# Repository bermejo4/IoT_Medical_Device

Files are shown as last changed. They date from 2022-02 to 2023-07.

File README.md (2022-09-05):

# IoT Medical Device Development:

## Objectives:
- Electronic wireless system to collect physiological data from a patient and deliver it to a server.
- Wireless. (without data cable or power cable)
- Low Cost.
- Small dimensions. 
- Show the information collected on the server.

## Steps: 
[Steps.md](https://github.com/bermejo4/Proyectos2/blob/main/Documentation/Steps.md)

## Costs:
[Costs.md](https://github.com/bermejo4/Proyectos2/blob/main/Documentation/Costs.md)

## Comparision between Raspberry Pico and Arduino Nano:
[ComparationBetween_RaspPico_ArduNano.md](https://github.com/bermejo4/Proyectos2/blob/main/Documentation/ComparationBetween_RaspPico_ArduNano.md)

## Pins-modules diagram:

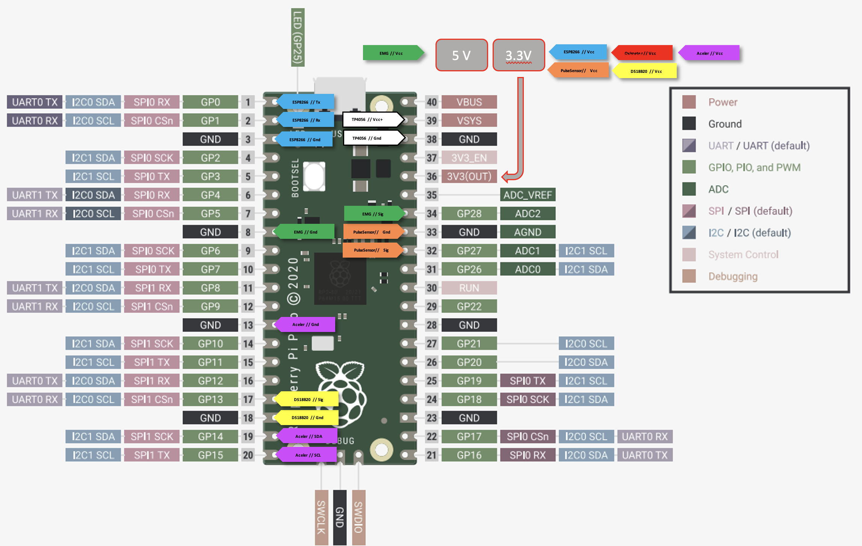
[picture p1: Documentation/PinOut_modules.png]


## Micropython code running on the Raspberry Pico:
[PicoClient/TCP_Send_info.py](https://github.com/bermejo4/Proyectos2/blob/main/PicoClient/TCP_Send_info.py)

## Server code:
[Server/tcp_graficador_pico.py ](https://github.com/bermejo4/Proyectos2/blob/main/Server/tcp_graficador_pico.py)

------
------
## Paper:

### Abstract
The aim of the present project is the development of a wireless, little size, low cost and scalable platform, based in IoT. It will be capable of measuring different physiological signals (temperature, pulse and movement) and internal device signals (temperature). Then, it will send them together in the same packet through Wi-Fi to a network, or the Internet, using the TCP/IP model to finally be received by a server and represented in a graphical format. The final use of it is to monitor patients in medical environments remotely by specialists.

### 1. Introduction
The Internet of Things (IoT) term refers to the collective network of connected devices and the technology that facilitates communication between devices and the cloud, as well as between the devices themselves [1]. In this context, Cisco states that IoT devices will account for 50
percent (14.7 billion) of all globally networked devices by 2023 [2].

There is no doubt that this technology is growing unstoppably and every day more companies and sectors incorporate it. One of the industries that will have to face this change will be the medical instrumentation industry to connect all its medical devices to the Internet, which, whatever their function, are ultimately intended to obtain very useful physiological data for later analysis and according to them an adequate decision making.

Nowadays, there is an abundance of proprietary IoT healthcare platforms, for example, Apple Watch Series 3 combined with “Health” App, or Samsung Galaxy Watch 4 and “Samsung Health” App, which can monitor the ECG, oximetry, steps or sleep. But these systems and devices are very expensive, with watches prices above 400$ and phones between 600$ and 1100$ (smartwatches can't work properly without a smartphone). In many cases, these products are not scalable or modifiable because don't provide open-source software or hardware, and technical documentation too. Also, they need to be connected through Bluetooth to the phone, so two connections (first Bluetooth, then Wi-Fi or 5G) must be established and the probabilities of failures increase. This architecture could be minimized by using only one connection to transfer data to the cloud.
Also, there are specialized healthcare monitoring IoT hardware platforms like Mysignals HW(Libelium). This device can collect a lot of physiological signals such as temperature, glucose in blood, electrocardiogram, electromyogram, etc. And all open source and scalable, due to it being based on Arduino. Another example of a multisensory hardware platform for measuring physiological signals is Bitalino, but it only works with Bluetooth and is too expensive, starting at 400$ the basic, being an educational platform. 
Nowadays, there is a tendency to create open-source IoT devices. The possible design of efficient medical IoT sensor nodes in terms of low-cost, low power consumption, and increased data accuracy based on open-source platforms are covered by Nikos Petrellis et al. [3]. Their solution is performed with an Arduino UNO attached to a Raspberry Pi, but the costs of these elements (together more than 60$ nowadays) are still high compared to this project objective. And Sugathan et al. [4] create a generic clothing technology to measure SPO2, electro dermal activity, and body temperature implemented with an Arduino Lily-pad, although they send data through serial communication and they don’t use a wireless model, indeed it's one of their future enhancements. 
From a broad point of view, the final destination of this project is the design and implementation of a platform based on IoT, improving the requirements followed by Nikos Petrellis, to monitor patients in a Hospital or old people's home in a non-intrusive way when it's not necessary.

### 2.	Technical Proposal
The main purpose is to develop a platform that reaches the following objectives:
- First, a wearable small size device with a wireless connection to transmit the data collected from its sensors, focusing on a TCP/IP model for that purpose.
- Second, a low cost system, using components easy to buy nowadays on the Internet and cheap compared with others actual similar models.
- Third, a concentrated multi-sensor device capable of measuring different physiological signals.
- Fourth, a scalable IoT project. Sensors could be replaced or added depending on pins available and the protocol connection used.
To fulfill these mentioned requirements, a system is designed based on the development of an IoT device to acquire physiological and internal device data by sensors; 
then the packeting (JSON) and transfer of them with a TCP/IP model and finally their reception in an extern server. 
The system process is as follows: 
1. Sensorization: This device works with 3 external sensors (temperature sensor, pulse sensor and accelerometer) and 1 internal sensor (MCU temperature).
The internal sensor helps to know how is the IoT device working and to control it. Knowing the temperature a problem with the device can be detected if the temperature grows extremely.
2. Data collection: sensors send  physical analog signal to the microcontroller which are sampled and quantified to transform them into manageable digital data. In some cases the signal is digitalized in an external module where the sensor is placed rather than in the microcontroller, in this case the microcontroller only has to collect the result following the communication protocol used by the module in question  (SPI, I2C, UART, or one of its own).
3. Formatting and Transfer: Once the microcontroller has the data, it must prepare them for shipment. It is important to detail a format for the shipment that is distinguishable later in the reception, clearly marking the distinction between data collected from different sensors. JSON, a text format for sending data, widely used, easy to handle both at source and destination, is used to send the data collected to the destination.
The data is packeting using TCP/IP headers and then sending to the network through Wi-Fi.
4. Reception: At the destination the data is unformat and stored differently depending on the sensor to which they belong. Subsequently, these data can be represented in many ways, using an array, a graph… In this case is represented using a real time graph.

### 3.	Architecture
The system architecture can be described from a topological network point of view, shown in Figure 1. 

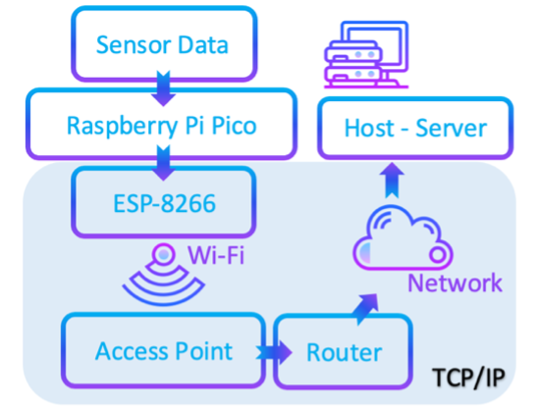
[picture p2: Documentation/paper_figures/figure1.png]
 

**Figure 1.** *Network topological architecture of the whole system.*

The device is set with an IP address and a port number. It transmits the information collected to an access point through Wi-Fi, and the access point sends the information to a router which decides where to send it. Once the information is sent through the Internet or a local network and then it arrives at the destination, a server.
This system uses TCP (Transmission Control Protocol) rather than UDP (User Datagram Protocol) to send the information to the remote host or server. The main differences between them are that TCP is a connection oriented and reliable protocol; and otherwise UDP is a connectionless and unreliable protocol. The data handled demands a reliable protocol because physiological data is dealt(it can be considered sensitive information). And an oriented connection protocol is needed because before to send the information the origin has to make sure that the destination is ready to receive it, although this kind of detail is less important than the reliable feature. Nevertheless, these TCP features pay its advantage in time, losing a little real time experience. It's true that UDP can be used implementing the TCP features in the application layer of TCP/IP model improving times, but also gaining more complexity, but this is out of the scope of this work.
An implementation detail to take account in the transfer step is the format of the information. All is encapsulated in a JSON format with the following shape:

```
{"Temp":"_","TempMcu":"_","PulseSig":"_","Acel_x":"_","Acel_y":"_","Acel_z":"_"}
```

Being the "_" the information of each field measured. Then, the destination knows this format and extract the information of each field to represent it properly.
When the information finally reaches the destination, it must be represented. For that purpose, a server code is written in Python that receive the data and represent it in a graphical format with the Matplotlib python library in real time. The server works with two threads, one has the task of receiving the data and save it, and the other thread represents the data in graphs, which are shown in the figure 2.

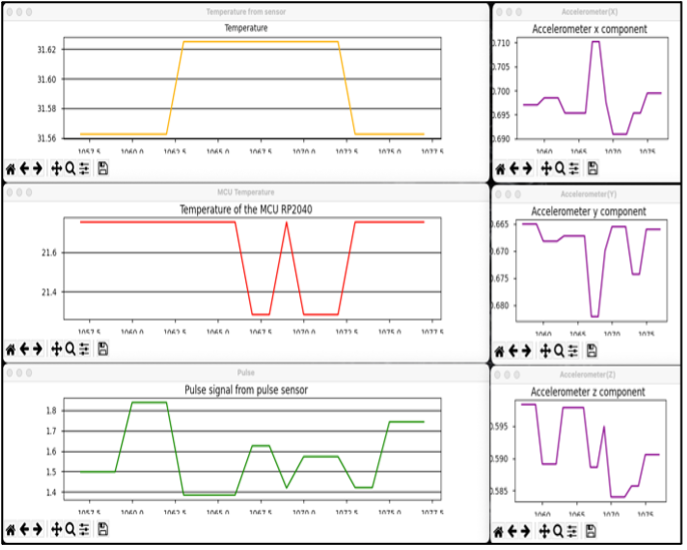
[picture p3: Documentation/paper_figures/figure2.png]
 

**Figure 2.** *Data representation with graphs.*

There are 6 graphs, one of the pulse sensor (green in Figure 2), another for the temperature (yellow in Figure 2), 3 for each of the axes of the accelerometer (purple in Figure 2) and other for the temperature of the mcu (red in the Figure 2). Each graph is represented in different windows, so the final user of the data can move and resize each graph depending on the screen size and which graph or graphs that are considered more important. Also, the Matplotlib frame representation gives some useful tools to manipulate the graphs. The server code is upload in [5].

### 4.	Implementation
The IoT device developed in this work uses:
**Temperature Sensor:** a sensor DS18B20 is used to measure the temperature which is connected to the Raspberry Pi Pico (GPIO 16) through a resistance of 4,7 kΩ (Figure 3 and Figure 6). It’s price is lower than 1$.

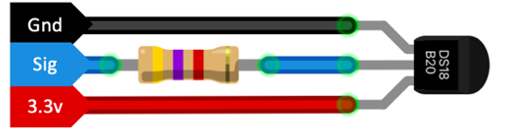
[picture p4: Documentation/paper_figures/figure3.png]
 

**Figure 3.** *DS18B20 connections with mcu.*

**Pulse Sensor:** to obtain the pulse a module called "Pulse Sensor for Arduino", built with an APDS-9008 photo sensor and MCP6001 Op-Amp, is connected directly to the pin 31 (ADC0) of the Raspberry Pi Pico. It sends an analogical signal to it, wire pink of the Figure 4. It’s price is around 1$ and 3$.

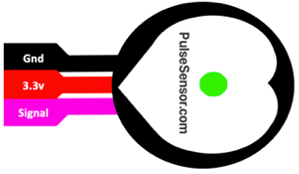
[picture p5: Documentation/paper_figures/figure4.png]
 

**Figure 4.** *Pulse Sensor connections with mcu.*

**Accelerometer:** To obtain the movements the MPU5060 board is used. It employs an I2C communication protocol, so it needs two I2C pins. The Slave Data Address pin (SDA) is connected to the pin SDA 19, and the Slave Clock pin (SCL) is connected to the pin SDA 20 (Figures 5 and 6). Its price is around 2$.

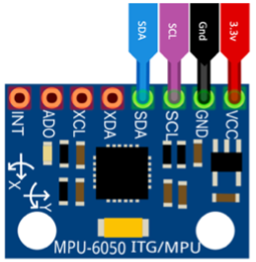
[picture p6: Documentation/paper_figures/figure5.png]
 

**Figure 5.**  *MPU5060 connections with mcu.*

**Microcontroller (mcu):** Raspberry Pi Pico has a dual core microcontroller chip (Rp2040) with a flexible clock of 133MHz, a SRAM of 264KB, 26 pins, 4 of it analog, two UART, two I2C and two SPI connections available. Also, there is a temperature sensor inside accessible with software to control mcu temperature. The price of this microcontroller is around 5$. All the connections are shown in the figure 6.
The Raspberry Pi Pico can be programmed with Micropython, C or C++. In this case the microcontroller has been programmed in Micropython, a lean and efficient implementation of the Python 3 programming language that includes a small subset of the Python standard library and is optimised to run on microcontrollers and in constrained environments.

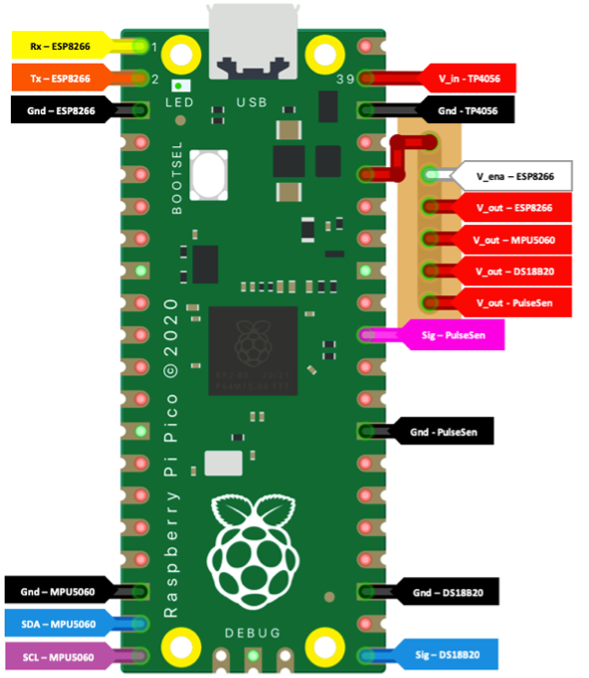
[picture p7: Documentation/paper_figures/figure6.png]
 

**Figure 6.** *Raspberry Pi Pico connections diagram.* 

**Wi-Fi Module:** The ESP8266 Module is used as a slave of the mcu through a UART connection. The connections of the wires must be done connecting Rx pin of the ESP8266 with the mcu Tx pin, and Tx of the ESP8266 with Rx mcu pin. Is necessary in some boards uses one pin of the ESP8266 fed with 3.3V to enable the UART mode (Figure 7). Its price is 1$.

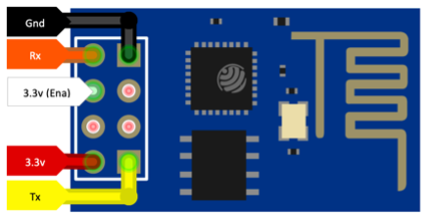
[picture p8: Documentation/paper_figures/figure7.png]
 

**Figure 7.** *ESP8266 connections with mcu, white wire enable UART mode.* 

The Wi-Fi module works with AT commands, which consists of a series of short text strings which can be combined to produce commands for operations such as dialing, hanging up, and changing the parameters of a connection; transmitted through the UART communication, so Micropython handles the commands in the form of strings to implement the corresponding communication protocol; some useful AT commands employed are: 
- AT: To test AT startup, also used to test the connection between the Raspberry Pi Pico and ESP8266.
- AT+CWJAP="Network_name","Password": To Search the Wi-Fi access point with the name "Network_name" and to connect to it with the password "Password".
- AT+CIPSTART="TCP","192.168.12.147",9999: To establish a TCP connection with a host or server with the IP address "192.168.12.147" and in the port "9999".
- AT+CIPSEND="Info_String": To send the information "Info_String" in the form of string through the connection established.

**Battery:** LiPo battery of 3.7 V, 1000 mAh, 10x20x50 mm size and its prize is around 5$. These features are very relevant, 3.7 V is the voltage that the microcontroller needs, dimensions match with its dimensions too, and the mAh will determine the durability of the battery depending on the total consume. 

**Battery Charger:** The TP4056 module is used as an intermediary between the battery, the microcontroller and the charger. It has a micro-usb plug, and two leds, red and blue. If red is blinking that means that the battery is charging, and if blue bright and red extinguish means charge termination. Two wires will be connected to the battery (Bat) and the other two will be connected to the mcu, one to power system pin (VSYS) and the other to ground (Gnd), showed in the Figure 8. Its price is 0.3$.

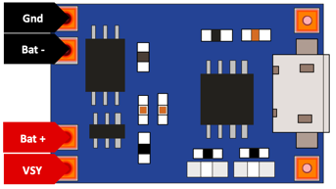
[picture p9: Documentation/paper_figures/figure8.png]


**Figure 8.**  *TP4056 connections with mcu and battery.* 

### 5.	Results
The final prototype of the device built is as the Figure 9AB shows, whose size is 20x40x50 mm. The global consume is 110 mA, so with a battery of 1000 mAh full charged the autonomy could be of more or less 9 hours, at best. The coverage area of the device depends on the coverage area of the ESP8266, and it depends on the access point technology and antenna, so it is conditional on each circumstance. 
A case is designed and printed in 3D with PLA to protect the device, and two straps have been added to attach the device to the arm, in the Figure 9CD.

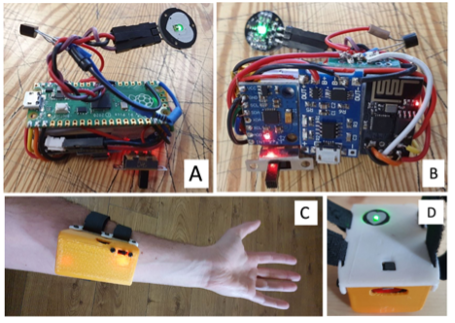
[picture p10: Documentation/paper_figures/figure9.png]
 

**Figure 9.** *Final device result.*

The final price of whole device is, looking up to, 17,3$ and with a conservative estimate 15$, depending on where the components are bought.
To test the system an access point is enabled with a smartphone where a computer and the IoT device are connected. First of all, the server must be running before to start the device, once it is, the device can be switched on, and after a little time of connection, between 3 or 5 seconds, the device begins to send the information to the server and when it receives it, the information is plotted in the graphs. 

### 6.	Conclusion
A prototype system have been developed fulfilled the objectives of low cost (15-17$), wireless, small size, scalable and capable of measure different physiological signals to send them after to a server where will be plotted.
This system may help in the future to monitor patients in a non-intrusive way by being placed in hospitals and complex care such as nursing homes, making real-time monitoring easier, cheaper and conserving resources, thus improving today's healthcare.
Future improvements encompass the utilization of MQTT protocols (MQTT message headers are small to optimize network bandwidth), also to publish each measure as a topic in a MQTT broker to permit other devices or services access to the information. It could improve the security with the encryption of the communication and the authentication of the IoT device with the server to avoid third entity in the client-server relationship. 
The project is upload in Github as open-source [6]. 

### Acknowledgements
Finally, I would like to express my gratitude to Eloy José Urendes Jiménez to help me to improve some details of this work. 

### References
[1]	Web of AWS where explain the terms around IoT: https://aws.amazon.com/es/what-is/iot/

[2]	Cisco, “Cisco Annual Internet Report (2018–2023) White Paper”, March 9 2020 : https://www.cisco.com/c/en/us/solutions/collateral/executive-perspectives/annual-internet-report/white-paper-c11-741490.html

[3]	Petrellis N, Birbas M, Gioulekas F. On the Design of Low-Cost IoT Sensor Node  e-Health Environments. Electronics. 2019; 8(2):178. https://doi.org/10.3390/electronics8020178

[4]	A. Sugathan, G. G. Roy, G. J. Kirthyvijay and J. Thomson. Application of arduino based platform for wearable health monitoring system, 2013 IEEE 1st International Conference on Condition Assessment Techniques in Electrical Systems (CATCON), 2013, pp. 1-5 (ISBN: 978-1-4799-0083-1).

[5]	Code in Github for the server that plots the information: https://github.com/bermejo4/IoT_Medical_Device/blob/main/Server/tcp_graficador_pico.py

[6]	All the documentation and code of this project: https://github.com/bermejo4/IoT_Medical_Device

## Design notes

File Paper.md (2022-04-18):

# Paper:
## Development of a medical monitoring system based on the internet of things

[posibles títulos]:
Desarrollo de un sistema de monitorización médica basado en internet de las cosas. 

-------
### Introduction:

The Internet of Things (IoT) term refers to the collective network of connected devices and the technology that facilitates communication between devices and the cloud, as well as between the devices themselves [1]. Nowadays everything is connected to the Internet from a computer or server to a fridge or a house, going through different industries and work environments to places of leisure or our own homes. In [2], Cisco, one of the huge networks company in the world, says that according to their analysis, IoT devices will account for 50 percent (14.7 billion) of all global networked devices by 2023. 

There is no doubt that this technology is growing unstoppably and every day more companies and sectors incorporate it. One of the industries that will have to face this change will be the medical instrumentation industry to connect all its medical devices to the Internet, which, whatever their function, are ultimately intended to obtain very useful physiological data for later analysis and according to them an adequate decision making.

There are an abundance of proprietary IoT healthcare platforms nowadays, for example, Apple Watch Series 3 [3] combined with "Health" App [4] can overwatch the ECG, the oximetry, steps or sleep. And the same its competitors like Samsung (Samsung Galaxy Watch 4 and "Samsung Health" App). But these systems and devices are very expensive together, with prices above 1000$, if you think about smartwathes can't work property without a smartphone. In many cases, these products are not scalable or modifiable because don't provide open-source software or hardware features.

Also, there are specialized healthcare monitoring IoT hardware platforms like Mysignals [5], property of Libelium, a IoT dedicated company. This product based on Arduino can collect a lot of physiological signals from sensors like Temperature, glucometer, ECG, EMG, SP02... And all open source, so it is more scalable than previous ones, or it was, because today MySignals is no longer available. Another example of multisensory hardware platform for measure physiological data is Bitalino [6], but it only works with Bluetooth and is too expensive being an educational platform. 

So many articles talk about the use of IoT for transmitting data acquire from the human body. In the work [7] authors cover the possible design of efficient medical IoT sensor nodes in terms of low-cost, low power-consumption, and increased data accuracy based on open-source platforms. It is performed with an Arduino UNO attached to a Raspberry Pi, but the costs of this elements (together more than 60$ nowadays) are still high compared to my proposal. And in [8] they create a generic clothing technology to measure SPO2, electro dermal activity, and body temperature implemented with an Arduino Lily-pad, although they don't send data through a wireless model, indeed it's one of their future enhancement. A wearable sensor-based human physical activity recognition is shown in the article [9] using MetaMotion Metawear as a sensor [10] and connecting it through Bluetooth to a smart-phone to send the data over the Internet to a Web Server. The problem with this is that two connections must be established as opposed to a single connection in my proposed model, and with each connection the probabilities of failures increase, so the architecture can be minimized using only one device, to transfer data to the cloud.

Bearing in mind everything said, current work focuses on the design and implementation of a device whom three sensors are connected, to measure temperature, pulse and movement, and send it through the Internet to a server that represents the data received graphically, to monitor patients of a Hospital or old people's home in a non-intrusive way when it's not necessary.

Within the context discussed above, this article tackles, the following targets:
- First, a wearable small size device with a wireless connection to transmit the data collected from its sensors, focusing on a TCP/IP model for that purpose.
- Second, a low cost system, less than 18$, using components easy to buy nowadays on the Internet and cheap compared with others actual models.
- Third, a scalable IoT project. It is used for a medical purpose, with 3 main sensors, but some others could replace them or be added depending on pins available and the protocol connection used, both in the medical field and for other field that we want, or indeed combined them, with only a few changes. 

~~It is expected that in the future most everyday objects will be connected to the Internet, for this the global industry will have to face the challenge of developing millions of devices that can connect to the Internet in an efficient way.~~

~~Many of the industries until now were only specialized in the creation of their product but now, in most cases, they must face the development and incorporation of a technology unknown to them that consists of the connectivity of their devices to the Internet, and for this they will have to allocate resources and money to this work, from specialized personnel to the purchase of material such as microcontrollers or network modules.~~

Today, thanks to advances in technology, it is possible to manufacture small IoT devices with ease because the size of the chips with which the network modules are manufactured are only a few centimeters in size and the cost is less than $2 per module, therefore manufacturing from scratch, or transforming a normal object into an IoT one, is quite affordable, making this new sector of technology grow unstoppably.

~~One of the industries that will have to face this change will be the medical instrumentation industry to connect all its medical devices to the Internet, which, whatever their function, are ultimately intended to obtain very useful physiological data for later analysis and according to them an adequate decision making.~~

There are some reasons about why is interesant to send data that are generated or collected by medical devices over the Internet. One of them is because many of the medical devices are usually small in size and to store all the data they collect they would need a memory built into the device, although the dimensions of the memory would not be much of a problem, the additional cost of this would be, depending on its capacity, and the subsequent inconvenience of having to dump all the data to a software running on a computer or server, therefore, moving to one of the following reasons, the data would not be seen in real time. Something that allows the Internet of Things is to monitor in real time, since the information as it is obtained is sent to the Internet instantly.
Regarding the issue of storage, thanks to the internet of things, we do not have to worry about having a memory in our device, since we can have a remote database, to which, thanks to the internet, we are sending all the data taken by our medical system.

Until now, the Internet of Things has only been discussed as a channel of reading and sending data, "monitoring", but the direction can be changed, and an external host, over the Internet of Things, can make responses accordingly to that data, and send it to our devices. It is true that if the device has a programmable microcontroller, these responses could be programmed without the need to incorporate the Internet of Things, but let's think bigger, let's think about how this device could be connected, for example, to an artificial intelligence located in a remote server or to a doctor, and that could offer answers according to a data pattern, for example the pulse of a person and a possible attack.

------- 
### Proporsal:

{Teniendo en cuenta los objetivos anteriormente mencionados mi propuesta para llevarlos a cabo es la creación de un sistema en el que el principal actor sea un dispositivo IoT desarrollado por mi cuyo funcionamiento se base en la recopilación de datos fisiológicos y del propio dispositivo mediante sensores; el empaquetamiento y el envío de ellos; y la recepción de estos en un sistema experto externo.
Podemos caracterizar ese sistema teniendo en mente la siguiente arquitectura:
- Sensorization.
- Data Collection.
- Formatting and Transfer.
- Reception and Decision making.}

Taking account the objetives recently described my proporsal to handle on is the development of a system in whch the main character will be an IoT device built by me whose function is based on the physiological patient and inter device data collection by sensors; then the packeting and transfer of them; and finally their reception in an extern system. Bearing in mind this, we can describe the system with the following architecture:
- Sensorization.
- Data Collection.
- Formatting and Transfer.
- Reception and Decision making.

~~As mentioned before, with today’s technology it is quite simple to develop a system based on the Internet of Things. With this in mind I have developed a low cost system based on the internet of things and whose main function is to monitor the temperature, pulse and movements of a patient; and send it all to an external server where it will be represented graphically for the future supervision of a professional or an artificial intelligence.~~ 
~~We can distinguish several phases that comprise in the operation of the system:~~

1. Sensorization:  A sensor is a device that produces an output signal from a physical phenomenon perceived. ~~One of the purposes of IoT is to transform all the real world phenomena into digital data to understand the world from a different point of view and for this task sensors are indispensable, helping humanity to perceive phenomena that sometimes they can not perceive on their on.~~
We can distinguish two classes of sensor in IoT; one is external sensor that helps the IoT device to develop its function, and the other is internal sensor that helps the IoT device to control how is everything about itself to care that it can develop its function without problems, and very often one kind of sensor is as important as the other.
The proposed device works with the following sensors:
    - 3 external sensors:
        - Temperature sensor. 
        - Pulse sensor.
        - Accelerometer.
    - 1 internal sensor:
        - Internal mcu temperature.
     
2. Data Collection:
~~The sensors send all physics phenomena which collect to a microcontroller in form of anolog signal (many of the physiological signals are signals of this kind), that sample and cuantificate~~  

The sensors send all the physical phenomenona which have been collected to a microcontroller in the form of an analog signal (the majority of physiological signals are signals of this type) that will be responsible for sampling and quantifying (assign numerical values to the input signal) to transform it into manageable digital data. In some cases the signal already comes digitalized from the sensors, in this case the microcontroller only has to collect it following the communication protocol used by the sensor in question (SPI, I2C, UART, or one of its own).

{Los sensores envían todos los fenomenos físicos que recopilan a un microcontrolador en forma de señal analógica (la gran mayoría de las señales fisiológicas son señales de este tipo) que se encargará de muestrear y cuantificar (asignar valores numéricos a la señal que llega) para así transformarla en datos digitales manejables. En algunos casos la señal ya viene de los sensores digitalizada, en este caso el microcontrolador solo tiene que recogerla siguiendo el protocolo de comunicación que utilice el sensor en cuestión.(SPI, I2C, UART, o uno propio)}

3. Formatting and Transfer.
Once the microcontroller has the data for a specific time, it must prepare them for shipment. It is important to detail a format for the shipment that is distinguishable later in the reception, clearly marking the distinction between data collected from different sensors. For this I chose to send them formatted by JSON, a text format for sending data, widely used, easy to handle both at source and destination.
The TCP/IP communication model is used to transfer the data.

{Una vez que el microcontrolador ya dispone de los datos correspondientes a un tiempo concreto, los debe preparar para el envío. Es importante detallar un formato para el envío que sea distinguible posteriormente en la recepción, marcando claramente la distinción entre datos recopilados de sensores diferentes. Para ello opté por enviarlos formateados mediante JSON, un formato de texto para el envío de datos ampliamente utilizado, fácil de manejar tanto en el origen como en el destino.
Para transferir los datos se utiliza el modelo de comunicación de redes TCP/IP. }

4. Reception and Decision making.

At the destination the data is unformat and stored depending on the sensor to which they belong, and depending, if there is more than one, on the microcontroller from where they come. Subsequently, these data can be represented in many ways, using an array, a graph... To facilitate the final work, which will be decision making. Depending on what the data set means, a decision will be made according to them, either by a medical entity or by an artificial intelligence

{En el destino los datos son desformateados y almacenados dependiendo del sensor al que pertenezcan, y dependiendo, si hubiera más de uno, del microcontrolador de donde provengan. Posteriormente esos datos se pueden representar de muchas maneras, mediante un array, una gráfica... Para facilitar así la labor final, que será la toma de decisión. Dependiendo de lo que signifique el conjunto de los datos se tomará una decisión acorde a ellos, ya sea por parte de una entidad médica o por una inteligencia artificial}

-------
### Implementation & configuration:
Materials and connections.
- Temperature Sensor: to measure the temperature I use a sensor called ds18b20 connected to the microcontroller through a resistance of 4,7 kOhms to the pin gpio X of the Raspberry Pi Pico. (Figure 2)
- Pulse Sensor: to obtain the pulse signal I use a module without a specific name, sometimes is called "Pulse Sensor for Arduino", connected directly to the pin gpio X of the Raspberry Pi Pico. It sends an analogical signal to it.(Figure 3)
- Accelerometer: To obtain the movements of the patient I use an accelerometer called mpu5060. It uses an I2C communication protocol, so it needs two I2C pins. The Slave Data Address pin (SDA) is connected to the pin X, and the Slave Clock pin (SCL) is connected to the pin X.(Figure 4)

- Microcontroller (mcu): Raspberry Pi Pico, this is the brain of the whole system. It has a dual core microcontroller chip (Rp2040) with a flexible clock of 133MHz, a SRAM of 264KB, 26 pins, 4 of it analog, two UART, two I2C and two SPI connections available. Also, there is a temperature sensor inside, accesible with software, to control mcu temperature. All the connections are shown in the figure 5.
- Wi-Fi Module: ESP8266, one of the most famous WiFi module boards. In this project is used as a slave of the mcu through a UART connection. It is important to say that the connections of the wires must be done connecting Rx pin of the ESP8266 with the mcu Tx pin, and Tx of the ESP8266 with Rx mcu pin. Is necessary in some boards uses one pin of the ESP8266 feeded with 3.3V to enable the UART mode. 

- Battery: LiPo battery of 3.7 V, 1000 mAh and 10x20x50 mm. These features are very relevant, 3.7 is the voltage that the microcontroller needs, dimensions match with its dimensions too, and the mAh will determine the durability of the battery depending on the whole consume.
- Battery Charger: The module used as an intermediary between the battery, the microcontroller and the charger is called TP4056. It has a micro-usb plug, and two leds, red and blue, if red is blinking that means that the battery is charging, anf if blue bright and red extinguish means charge termination. Two wires will be connected to the Battery (Bat) and the other two will be connected to the mcu, one to power system pin (VSYS) and the other to the ground (Gnd) as is showed in the Figure 6.

Once everything is connected it's time to configure the device with code. The Raspberry Pi Pico can be programmed with Micropython, C or C++. In this case the microcontroller has been programmed in Micropython, a lean and efficient implementation of the Python 3 programming language that includes a small subset of the Python standard library and is optimised to run on microcontrollers and in constrained environments [11]. It is important to say too that the ESP8266 works with AT commands, which consists of a series of short text strings which can be combined to produce commands for operations such as dialing, hanging up, and changing the parameters of a connection [12], transmitted through the UART communication, so Micropython handles the commands in the form of strings to implement the corresponding communication protocol; some useful AT commands employed are: 
- AT: To test AT startup, also used to test the connection between the Rapberry Pi Pico and ESP8266.
- AT+CWJAP="Network_name","Password" : To Search the Wi-Fi access point with the name "Network_name" and to connect to it with the password "Password".
- AT+CIPSTART="TCP","192.168.12.147",9999 : To establish a TCP connection with a host with the IP address "192.168.12.147" and the port "9999".
- AT+CIPSEND="String" : To send the information "String" in the form of string through the connection established.

To understand the protocols used in the whole system previously the system must be described from a topological network point of view. The device transmit the information collected to a access point though Wi-Fi, and the access point send the information to a router which decides where send it. Once the information is sent though the Internet or a local network it arrives to the destination, a host or a server, as represent the Figure 8.

Once the architecture of the system is understood, the protocols employed can be described. Bearing in mind the TCP/IP model and the third layer (transport layer) protocols, this system use TCP (Transmission Control Protocol) rather than UDP (User Datagram Protocol) to send the information to the remote host or server. The main differences between them are that TCP is a connection oriented and reliable protocol; and otherwise UDP is a connectionless and unreliable protocol. The data handled demands a reliable protocol because we are dealing with physiological data (can be considered sensitive data, one error in the data means that the patient is not ok). And a oriented connection protocol is needed because before to send the information we have to make sure that the destination is ready to receive it, although this kind of detail is less important than the reliable feature. Nevertheless, these TCP features pay its advantage in time, losing a little real time experience. It's true that UDP can be used to implement the features of TCP in the application layer of TCP/IP model improving times, but also gaining more complexity, this is out of the scope of this work.

An implementation detail to take account in the transfer step is the format of the information. All is encapsulated in a JSON format with the following shape:
{"Temp":"_","TempMcu":"_","PulseSig":"_","Acel_x":"_","Acel_y":"_","Acel_z":"_"}
Being the "_" the information of each field measured. Then, the destination knows this format and extract the information of each field to represent it properly. 

When the information finally reaches the destination it must be represented. For that purpose I write a server code in Python that receive the data and represent it in a graphical format with the Matplotlib[13] python library in real time. The code can be found here [14]. The server works with two threads one has the task of receiving the data and save it, and the other thread represents the data in graphs. There are 6 graphs, one of the pulse, another for the Temperature, 3 for each of the axes of the accelerometer and other for the temperature of the mcu.

-------
### Test and Results:

The final result of the device built is as the Figure 10 shows, It is a gadget of 20x40x50mm size. The whole consume is 110mA, so with a battery of 1000mAh full charged the autonomy could be of more or less 9 hours, at best. The coverage area of the device depends on the coverage area of the ESP8266, and it depends on the access point technology and antenna, so it is conditional on each circumstance, but some experiments have proven that with a normal access point the coverage area could be about 300 meters without obstacles [15].

To test the system an access point is enabled with a smartphone where a computer and the IoT device are connected. First of all, the server must be running before to start the device, once it is, the device can be switched on, and after a little time of connection,between 3 or 5 seconds, the device begins to send the information to the server and when it receives it, the information is plotted in the graphs.

-------
### Conclusion & Future Improvements.

Este sistema podrá ayudar en un futuro a la supervisión de pacientes de una forma no intrusiva colocandose en hospitales y complejos asistenciales como residencia de ancianos, haciendo que el monitoreo en tiempo real sea más sencillo, barato y preservando recursos, mejorando así la sanidad de hoy en día.

This system may help in the future to monitor patients in a non-intrusive way by being placed in hospitals and complex care such as nursing homes, making real-time monitoring easier, cheaper and conserving resources, thus improving today's healthcare.

Future improvements encompass the utilization of MQTT protocols (MQTT message headers are small to optimize network bandwidth [16]), also to publish each measure as a topic in a MQTT broker to permit other devices or services access to the information. Something to improve the security could be the encryption of the communication and the authentication of the IoT device with the server to avoid third entity in the client-server relationship. And finally to make a comfortable user experience other improvement can be a Bi-directional communication to send instructions to the IoT device like the modification of the sampling rate.

-------  

-------
-------
## Paper español:

#### Intro:

{Se prevee que en un futuro la mayoría de los objetos cotidianos estén conectados a internet, para ello la industria global deberá afrontar el reto de desarrollar millones de dispositivos que puedan conectarse a internet de una forma eficaz. 

Muchas de las industrias hasta el momento solo estaban especializadas en la creación de su producto pero ahora, en la mayoría de los casos,  deben hacer frente al desarrollo e incorporación de una tecnología desconocida para ellos que consiste en la conectividad de sus aparatos a internet, y para ello tendrán que destinar recursos y dinero a esta labor, desde personal especializado hasta las compra de material como microcontroladores o módulos de red.  

Hoy en día, gracias a los avances de la tecnología es posible fabricar pequeños dispositivos IoT con facilidad debido a que el tamaño de los chips con los que se fabrican los modulos de red son de apenas unos centímetros de tamaño y el coste es de menos de 2$ por modulo, por lo tanto fabricar de cero, o transformar un objeto normal en uno IoT, es bastante asequible haciendo que este nuevo sector de la tecnología crezca imparablemnte. 

Una de las industrias que deberán hacer frente a este cambio será la industria de la instrumentación médica para conectar a internet todos sus aparatos médicos, que sea cual sea su función en última instancia están destinados a la obtención de datos fisiológicos muy útiles para su posterior análisis y acorde a ellos una toma de decisión adecuada.

Hay algunas razones por las que es interesante enviar datos generados o recopilados por dispositivos médicos a través de Internet. Una de ellas es porque muchos de los dispositivos médicos suelen ser de pequeño tamaño y para almacenar todos los datos que recopilan necesitarían una memoria incorporada al aparato, si bien las dimensiones de la memoría no serían mucho problema, si que lo sería el coste adicional de esta dependiendo de su capacidad y la posterior molestia de tener que volcar todos los datos a un software corriendo en un ordenador o servidor, por lo tanto, pasando a uno de las siguientes motivos, los datos ya no serían en tiempo real. Algo que permite internet de las cosas es monitorear en tiempo real, ya que la información según se obtiene se envía a internet en el instante. 
Con respecto al tema del almacenamiento gracias a internet de las cosas no tenemos que preocuparnos en tener una memoria en nuestro aparato ya que podemos tener una base de datos remota a la que gracias a internet estemos enviando todos los datos tomados por nuestro sistema médico.

Hasta el momento solo se ha hablado del internet de las cosas como un medio de lectura y envío de datos, "monitoreo", pero se puede cambiar el sentido, y que un equipo externo, a través de internet de las cosas, efectue respuestas acorde a esos datos y las envíe a nuestro aparato. Es verdad, que si el aparato dispone de un microcontrolador programable esas respuestas se podrían programar sin la necesidad de incorporar internet de las cosas, pero pensemos más a lo grande, pensemos como ese aparato se podría conectar por ejemplo a una inteligencia artificial ubicada en un servidor remoto , y que pudiese ofrecer respuestas acorde a un patron de datos, por ejemplo el pulso de una persona y un posible ataque.
}

#### Propuesta:

{Como se ha mencionado antes, con la tecnología de hoy en día es bastante sencillo desarrollar un sistema basado en internet de las cosas. ~~para monitorear parametros fisiológicos de un paciente y así ayudar en el diagnisto o control de él~~. Teniendo esto en cuenta he desarrollado un sistema de bajo coste basado en internet de las cosas y cuya función principal es monitorear la temperatura, pulso y movimientos de un paciente; y enviar todo ello a un servidor externo donde será representado graficamente para la futura supervisión de un profesional o de una inteligencia artificial. 
Podemos distinguir varias fases que comprenden en el funcionamiento del sistema:}

-------
-------

1. Introducción.
    - ¿Qué sería?
        - Plataforma educativa.
        - IOT.
        - IA.
        - Señales fisiológicas.
        - Modulo de control, seguimiento, control de patologías.
    - ¿Que hay ya hoy en día?
    - Propuesta.

2. Propuesta-plataforma.
3. Implementación.
4. Pruebas/resultados.
    - Técnico:
        - Latencia.
        - Información.
        - TCP/UDP.
    - Usabilidad:
        - Caminar con ello puesto.

5. Conclusión/Trabajos futuros.
6. +ANEXOS (código servidores y placa)

----

Bibliografía:

referencias:
[1] https://aws.amazon.com/es/what-is/iot/ 
[2] "Cisco Annual Internet Report (2018–2023) White Paper": https://www.cisco.com/c/en/us/solutions/collateral/executive-perspectives/annual-internet-report/white-paper-c11-741490.html
[3] https://www.apple.com/es/healthcare/apple-watch/
[4] https://www.apple.com/es/ios/health/
[5] http://www.my-signals.com/ 
[6] https://bitalino.com/
[7] https://www.mdpi.com/2079-9292/8/2/178
[8] Application of Arduino Based Platform for Wearable Health Monitoring System.
[9] Wearable Internet-of-Things platform for human activity recognition and health care.
[10] https://mbientlab.com/metamotionr/
[11] https://micropython.org/
[12] https://en.wikipedia.org/wiki/Hayes_command_set
[13] https://matplotlib.org/
[14] https://github.com/bermejo4/Proyectos2/blob/main/Server/tcp_graficador_pico.py
[15] https://www.youtube.com/watch?v=7BYdZ_24yg0 time 1:42 start the experiment without add other antenna.
[16] https://mqtt.org/

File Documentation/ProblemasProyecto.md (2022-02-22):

# Principales Problemas durante el proyecto:

- Sensor de pulso mete mucho ruido. Y con excasas variaciones en el sensor se producen altas oscilaciones en la medida.
  - Solución: con sofware guardar una estimación de la media de los últimos 10 segundos y todo lo que la sobrepase es un pulso.

- Módulos normalmente usados para Arduino usan librerías de c y no usan micropython.
  - Solución: (muy costosa), intentar traducir de c a micropython la librería. 

- Raspberry pico no soporta todas las librerías de micropython.
  - Solución: leer bien la documentación e investigar que función puede sustituir a la que se usa en esa librería.

- Puertos analógicos insuficientes en un futuro posiblemente.
  - Posible problema si uso todos los sensores que inicialmente pensé. Todavía no he llegado a ese punto. No doy un sensor como definitivo hasta que no se demuestra funcionar correctamente.

- No hay módulo de EMG en el mercado que sea barato.
  - Solución: Fabricar uno a partir de resistencias, amplificadores y condensadores.

- No hay modulo de oximetría en el mercado, el único que existe son todos malos y se ha dejado de fabricar.
  - Solución: Pedir uno por aliexpress.

- No funciona el módulo MPU6050 que hace de acelerometro. Funcionó un día, pero luego ya no funcionaba. Probé a cambiar de modulo mpu6050, pero daba el mismo error, probé a cambiar de placa raspberry pi pico, pero igualmente daba el mismo error, probé a cambiar el mpu5060 a Arduino y funcionó, por lo tanto concluí que el error estaba en el código. 
  - Solución: Encontré otro código compatible tanto con raspberry pi pico como con el módulo MPU6050.

- El servidor no podía decodificar la información que le llegaba. Los pines tx y rx de la pico y del esp8266 estaban mal emparejados. La conexion estre ellos debe ser de tx-rx y rx-tx, ;y no tx-tx y rx-rx. Solución: cambiar los cables emparejados.

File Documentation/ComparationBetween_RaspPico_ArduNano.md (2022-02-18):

# Commparation between Raspberry Pico and Arduino Nano

|  Commparation | Raspberry Pico | Arduino Nano |
| -- | -- | -- |
| Price | 6 € | 18 € |
| MCU Chip | Dual Core (Rp2040) | One Core (ATmega328) |
| Clock| Flexible 133 MHz | 16 MHz |
| SRAM | 264 KB | 2 KB |
| EEPROM | 0 KB | 1 KB |
| Input Power |  1.8 - 5.5 Vdc| 7 - 12 Vdc |
| Pin I/O | 26 (16 PWM) | 22 (6 PWM) |
| Analog Pins | 4 | 8 |
| Communicacation | 2x UART, 2x I2C, 2x SPI | 1x UART, 1x I2C, 1x SPI |
| Additional | Timer with 4 alarms, Real Time Counter | -- |
| Output Voltage | 3.3 V | 5 V |
| Flash | 2 MB | 32 KB |
| Processing Bits | 32 bits | 8 bits |
| Programming | Micropython and C/C++ | C/C++ |
| IDE | Thonny | Arduino_IDE or Visual |
| PCB Size | 21 x 51 mm | 18 x 45 mm |

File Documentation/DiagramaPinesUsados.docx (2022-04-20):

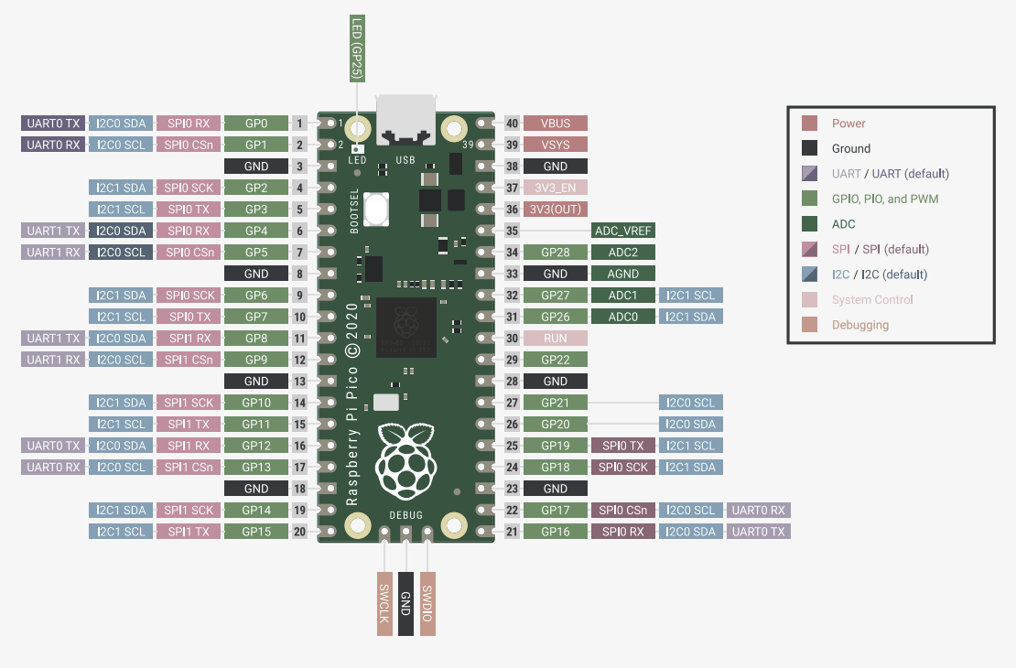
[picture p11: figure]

ESP8266 // Tx

ESP8266 // Rx

PulseSensor// Sig

Aceler // Vcc

TP4056 // Gnd

TP4056 // Vcc+

Aceler // Gnd

DS18B20 // Sig

Aceler // SDA

Aceler // SCL

DS18B20 // Vcc

PulseSensor// Vcc

ESP8266 // Vcc

3.3V

DS18B20 // Gnd

PulseSensor// Gnd

ESP8266 // Gnd

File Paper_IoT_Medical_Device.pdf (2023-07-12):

# Development of a medical monitoring system based on the Internet of Things

### J. Bermejo Torres

Higher Polytechnic School, San Pablo CEU University, Madrid, Spain, j.bermejo1@usp.ceu.es

### Abstract

The aim of the present project is the development of a wireless, little size, low cost and scalable platform, based in IoT. It will be capable of measure different physiological signal (temperature, pulse and movement) and internal device signal (temperature). Then, it will send them together in the same packet through Wi-Fi to a network, or the Internet, using the TCP/IP model to finally be received by a server and represented it in a graphical format. The final use of it is to monitor patients in medical environments remotely by specialists.

### 1. Introduction

The Internet of Things (IoT) term refers to the collective network of connected devices and the technology that facilitates communication between devices and the cloud, as well as between the devices themselves [1]. In this context, Cisco states that IoT devices will account for 50 percent (14.7 billion) of all global networked devices by 2023 [2].
There is no doubt that this technology is growing unstoppably and every day more companies and sectors incorporate it. One of the industries that will have to face this change will be the medical instrumentation industry to connect all its medical devices to the Internet, which, whatever their function, are ultimately intended to obtain very useful physiological data for later analysis and according to them an adequate decision making. Nowadays, there is an abundance of proprietary IoT healthcare platforms, for example, Apple Watch Series 3 combined with “Health” App, or Samsung Galaxy Watch 4 and “Samsung Health” App, can monitor the ECG, the oximetry, steps or sleep. But these systems and devices are very expensive, with watches prices above 400$ and phones between 600$ and 1100$ (smartwatches can't work properly without a smartphone). In many cases, these products are not scalable or modifiable because don't provide open-source software or hardware, and technical documentation too. Also, they need to be connected through bluetooth to the phone, so two connections (first bluetooth, then Wi-Fi or 5G) must be established and the probabilities of failures increase. This architecture could be minimized using only one connection to transfer data to the cloud.
Also, there are specialized healthcare monitoring IoT hardware platforms like Mysignals HW(Libelium). This device can collect a lot of physiological signals such as temperature, glucose in blood, electrocardiogram, electromyogram, etc. And all open source and scalable, due to it is based on Arduino. Another example of
multisensory | hardware | platform | for | measure
physiological signals is Bitalino, but it only works with Bluetooth and is too expensive, starting at 400$ the basic, being an educational platform.
Nowadays, there is a tendency to create open source IoT devices. The possible design of efficient medical IoT sensor nodes in terms of low-cost, low power-consumption, and increased data accuracy based on open-source platforms is covered by Nikos Petrellis et al. [3]. Their solution is performed with an Arduino UNO attached to a Raspberry Pi, but the costs of these elements (together more than 60$ nowadays) are still high compared to this project objective. And Sugathan et al.
[4] create a generic clothing technology to measure SPO2, electro dermal activity, and body temperature implemented with an Arduino Lily-pad, although they send data through serial communication and they don’t use a wireless model, indeed it's one of their future enhancements.
From a broad point of view, the final destination of this project is the design and implementation of a platform based in IoT, improving the requirements followed by Nikos Petrellis, to monitor patients of a Hospital or old people's home in a non-intrusive way when it's not necessary.

### 2. Technical Proposal

The main purpose is to develop a platform that reaches the following objectives:
- First, a wearable small size device with a wireless connection to transmit the data collected from its sensors, focusing on a TCP/IP model for that purpose.
- Second, a low cost system, using components easy to buy nowadays on the Internet and cheap compared with others actual similar models.
- Third, a concentrated multi-sensor device capable of measuring different physiological signals.
- Fourth, a scalable IoT project. Sensors could be replaced or added depending on pins available and the protocol connection used.
To fulfill these mentioned requirements, a system is designed based on the development of an IoT device to acquire physiological and internal device data by sensors;

then the packeting (JSON) and transfer of them with a TCP/IP model and finally their reception in an extern server.
The system process is as follows:
1. Sensorization: This device works with 3 external sensors (temperature sensor, pulse sensor and accelerometer) and 1 internal sensor (MCU temperature). The internal sensor helps to know how is the IoT device working and to control it. Knowing the temperature a problem with the device can be detected if the temperature grows extremely.
2. Data collection: sensors send physical analog signal to the microcontroller which are sampled and quantified to transform them into manageable digital data. In some cases the signal is digitalized in an external module where the sensor is placed rather than in the microcontroller, in this case the microcontroller only has to collect the result following the communication protocol used by the module in question (SPI, I2C, UART, or one of its own).
3. Formatting and Transfer: Once the microcontroller has the data, it must prepare them for shipment. It is important to detail a format for the shipment that is distinguishable later in the reception, clearly marking the distinction between data collected from different sensors. JSON, a text format for sending data, widely used, easy to handle both at source and destination, is used to send the data collected to the destination.
The data is packeting using TCP/IP headers and then sending to the network through Wi-Fi.
4. Reception: At the destination the data is unformat and stored differently depending on the sensor to which they belong. Subsequently, these data can be represented in many ways, using an array, a graph… In this case is represented using a real time graph.

### 3. Architecture

The system architecture can be described from a topological network point of view, shown in Figure 1.

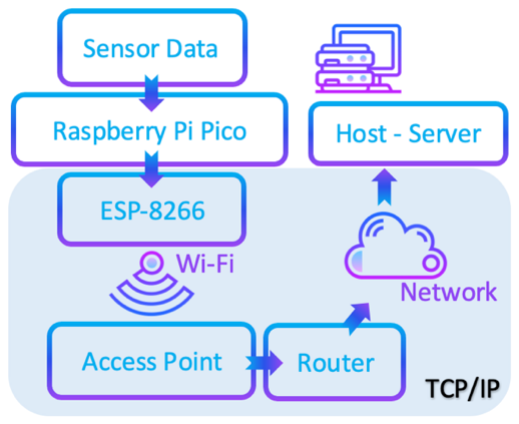
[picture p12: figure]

Figure 1. Network topological architecture of the whole system.

The device is setting with an IP address and a port number. It transmits the information collected to an access point through Wi-Fi, and the access point sends the information to a router which decides where send it. Once the information is sent through the Internet or a local network and then it arrives to the destination, a server. This system uses TCP (Transmission Control Protocol) rather than UDP (User Datagram Protocol) to send the information to the remote host or server. The main differences between them are that TCP is a connection oriented and reliable protocol; and otherwise UDP is a connectionless and unreliable protocol. The data handled demands a reliable protocol because physiological data is dealt(it can be considered sensitive information). And an oriented connection protocol is needed because before to send the information the origin has to make sure that the destination is ready to receive it, although this kind of detail is less important than the reliable feature. Nevertheless, these TCP features pay its advantage in time, losing a little real time experience. It's true that UDP can be used implementing the TCP features in the application layer of TCP/IP model improving times, but also gaining more complexity, but this is out of the scope of this work.
An implementation detail to take account in the transfer step is the format of the information. All is encapsulated in a JSON format with the following shape:

Being the "_" the information of each field measured. Then, the destination knows this format and extract the information of each field to represent it properly.
When the information finally reaches the destination, it must be represented. For that purpose, a server code is written in Python that receive the data and represent it in a graphical format with the Matplotlib python library in real time. The server works with two threads, one has the task of receiving the data and save it, and the other thread represents the data in graphs, which are shown in the figure 2.

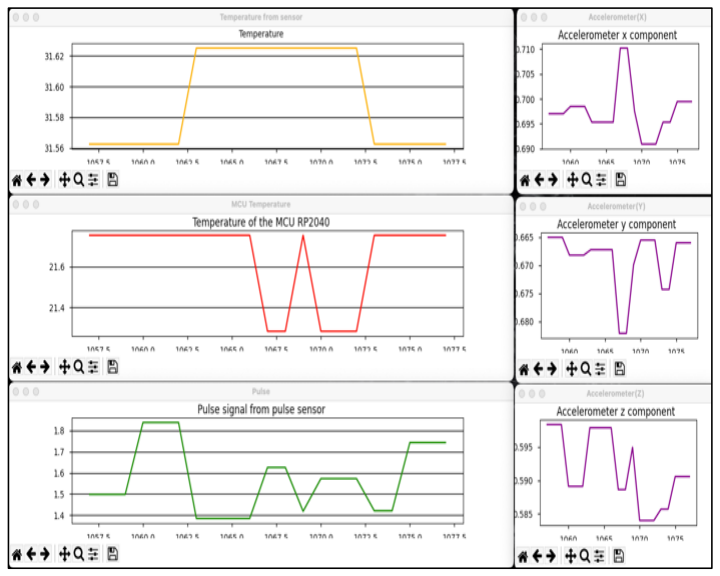
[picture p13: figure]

Figure 2. Data representation with graphs. There are 6 graphs, one of the pulse sensor (green in Figure 2), another for the temperature (yellow in Figure 2), 3 for each of the axes of the accelerometer (purple in Figure 2) and other for the temperature of the mcu (red in the Figure 2). Each graph is represented in different

{"Temp":"_","TempMcu":"_","PulseSig":"_", "Acel_x":"_","Acel_y":"_","Acel_z":"_"}

windows, so the final user of the data can move and resize each graph depending on the screen size and which graph or graphs that are considered more important. Also, the Matplotlib frame representation gives some useful tools to manipulate the graphs. The server code is upload in [5].

### 4. Implementation

The IoT device developed in this work uses
Temperature Sensor: a sensor DS18B20 is used to measure the temperature which is connected to the Raspberry Pi Pico (GPIO 16) through a resistance of 4,7 kΩ (Figure 3 and Figure 6). It’s price is lower than 1$.

Figure 3. DS18B20 connections with mcu.
Pulse Sensor: to obtain the pulse a module called "Pulse Sensor for Arduino", built with an APDS-9008 photo sensor and MCP6001 Op-Amp, is connected directly to the pin 31 (ADC0) of the Raspberry Pi Pico. It sends an analogical signal to it, wire pink of the Figure 4. It’s price is around 1$ and 3$.

Figure 4. Pulse Sensor connections with mcu.

Accelerometer: To obtain the movements the MPU5060 board is used. It employs an I2C communication protocol, so it needs two I2C pins. The Slave Data Address pin (SDA) is connected to the pin SDA 19, and the Slave Clock pin (SCL) is connected to the pin SDA 20 (Figure 5 and 6). Its price is around 2$.

Figure 5. MPU5060 connections with mcu.

Microcontroller (mcu): Raspberry Pi Pico has a dual core microcontroller chip (Rp2040) with a flexible clock of 133MHz, a SRAM of 264KB, 26 pins, 4 of it analog, two UART, two I2C and two SPI connections available. Also, there is a temperature sensor inside accessible with software to control mcu temperature. The price of this microcontroller is around 5$. All the connections are shown in the figure 6.
The Raspberry Pi Pico can be programmed with Micropython, C or C++. In this case the microcontroller has been programmed in Micropython, a lean and efficient implementation of the Python 3 programming language that includes a small subset of the Python standard library and is optimised to run on microcontrollers and in constrained environments.

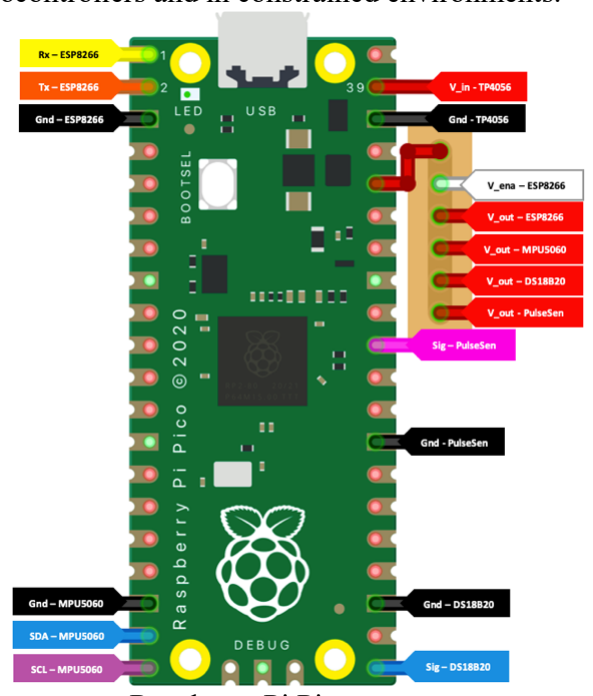
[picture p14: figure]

Figure 6. Raspberry Pi Pico connections diagram.

Wi-Fi Module: The ESP8266 Module is used as a slave of the mcu through a UART connection. The connections of the wires must be done connecting Rx pin of the ESP8266 with the mcu Tx pin, and Tx of the ESP8266 with Rx mcu pin. Is necessary in some boards uses one pin of the ESP8266 fed with 3.3V to enable the UART mode (Figure 7). Its price is 1$.

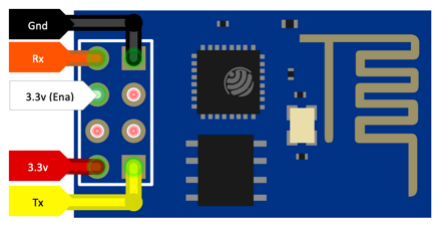
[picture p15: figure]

Figure 7. ESP8266 connections with mcu, white wire enable UART mode.
The Wi-Fi module works with AT commands, which consists of a series of short text strings which can be combined to produce commands for operations such as dialing, hanging up, and changing the parameters of a
connection; | transmitted | through | the | UART
communication, so Micropython handles the commands in the form of strings to implement the corresponding communication protocol; some useful AT commands employed are:
- AT: To test AT startup, also used to test the connection between the Raspberry Pi Pico and ESP8266.
- AT+CWJAP="Network_name","Password": To Search the Wi-Fi access point with the name "Network_name" and to connect to it with the password "Password".
- AT+CIPSTART="TCP","192.168.12.147",9999: To establish a TCP connection with a host or server with the IP address "192.168.12.147" and in the port "9999".

- AT+CIPSEND="Info_String": | To | send | the
information "Info_String" in the form of string through the connection established.
Battery: LiPo battery of 3.7 V, 1000 mAh, 10x20x50 mm size and its prize is around 5$. These features are very relevant, 3.7 V is the voltage that the microcontroller needs, dimensions match with its dimensions too, and the mAh will determine the durability of the battery depending on the total consume.
Battery Charger: The TP4056 module is used as an intermediary between the battery, the microcontroller and the charger. It has a micro-usb plug, and two leds, red and blue. If red is blinking that means that the battery is charging, and if blue bright and red extinguish means charge termination. Two wires will be connected to the battery (Bat) and the other two will be connected to the mcu, one to power system pin (VSYS) and the other to ground (Gnd), showed in the Figure 8. Its price is 0.3$.

Figure 8. TP4056 connections with mcu and battery.

### 5. Results

The final prototype of the device built is as the Figure 9AB shows, whose size is 20x40x50 mm. The global consume is 110 mA, so with a battery of 1000 mAh full charged the autonomy could be of more or less 9 hours, at best. The coverage area of the device depends on the coverage area of the ESP8266, and it depends on the access point technology and antenna, so it is conditional on each circumstance.
A case is designed and printed in 3D with PLA to protect the device, and two straps have been added to attach the device to the arm, in the Figure 9CD.

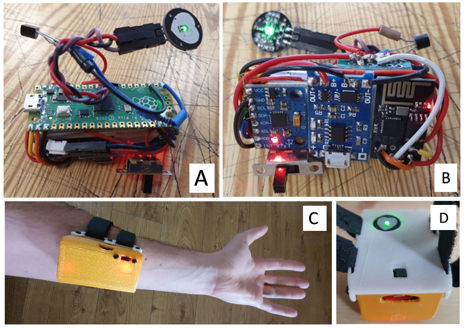
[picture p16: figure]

Figure 9. Final device result.

The final price of whole device is, looking up to, 17,3$ and with a conservative estimate 15$, depending on where the components are bought.
To test the system an access point is enabled with a smartphone where a computer and the IoT device are connected. First of all, the server must be running before to start the device, once it is, the device can be switched on, and after a little time of connection, between 3 or 5 seconds, the device begins to send the information to the server and when it receives it, the information is plotted in the graphs.

### 6. Conclusion

A prototype system have been developed fulfilled the objectives of low cost (15-17$), wireless, small size, scalable and capable of measure different physiological signals to send them after to a server where will be plotted.
This system may help in the future to monitor patients in a non-intrusive way by being placed in hospitals and complex care such as nursing homes, making real-time monitoring easier, cheaper and conserving resources, thus improving today's healthcare.
Future improvements encompass the utilization of MQTT protocols (MQTT message headers are small to optimize network bandwidth), also to publish each measure as a topic in a MQTT broker to permit other devices or services access to the information. It could improve the security with the encryption of the communication and the authentication of the IoT device with the server to avoid third entity in the client-server relationship.
The project is upload in Github as open-source [6].

### Acknowledgements

Finally, I would like to express my gratitude to Eloy José Urendes Jiménez to help me to improve some details of this work.

### References

[1] Web of AWS where explain the terms around IoT: https://aws.amazon.com/es/what-is/iot/
[2] Cisco, “Cisco Annual Internet Report (2018–2023) White
Paper”, | March | 9 | 2020 | :
https://www.cisco.com/c/en/us/solutions/collateral/executive-perspectives/annual-internet-report/white-paper-c11-741490.html
[3] Petrellis N, Birbas M, Gioulekas F. On the Design of Low-
Cost | IoT | Sensor | Node | e-Health
Environments. Electronics. | 2019; | 8(2):178.
https://doi.org/10.3390/electronics8020178
[4] A. Sugathan, G. G. Roy, G. J. Kirthyvijay and J. Thomson. Application of arduino based platform for wearable health monitoring system, 2013 IEEE 1st International Conference on Condition Assessment Techniques in Electrical Systems (CATCON), 2013, pp. 1-5 (ISBN: 978-1-4799-0083-1).
[5] Code in Github for the server that plots the information: https://github.com/bermejo4/IoT_Medical_Device/blob/main/Server/tcp_graficador_pico.py
[6] All the documentation and code of this project: https://github.com/bermejo4/IoT_Medical_Device

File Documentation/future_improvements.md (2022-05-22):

- Encriptación
- MQTT protocol
- MQTT broker
- Autentificación
- Mejora del graficador (grafana)
- Configurar Ip, hacer que el dispositivo inicialmente sea un servidor (por ejemplo web),
y se le pueda configurar facilmente la ip mendiante un formulario sencillo, y luego cambie el roll a cliente.
- pueda descargarse la última versión de mi repo de github.
- boton de reset para la anterior configuración.
- poner el sistema en bajo consumo.

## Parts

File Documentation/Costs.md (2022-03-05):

# Costs:
--------
### Main costs of the project:

|  Component | Price | Source |
| -- | -- | -- |
| Raspberry Pico | 4,20 € | https://www.kubii.es/raspberry-pi-3-2-b/3205-raspberry-pi-pico-0728886755172.html?src=raspberrypi |
| ESP8266 | 2,99 € | https://www.az-delivery.de/es/products/esp8266-01?variant=6119652786203 |
| Pulse Sensor Module | 1,38 - 6,99 € | Aliexpress - Amazon |
| MPU6050 | 2,2 € | Amazon |
| DS18B20 | 1,04 € | Amazon |
| Battery | 4,29 € | Aliexpress |
|  |  |  |
| Total | 16,01 € | -- |

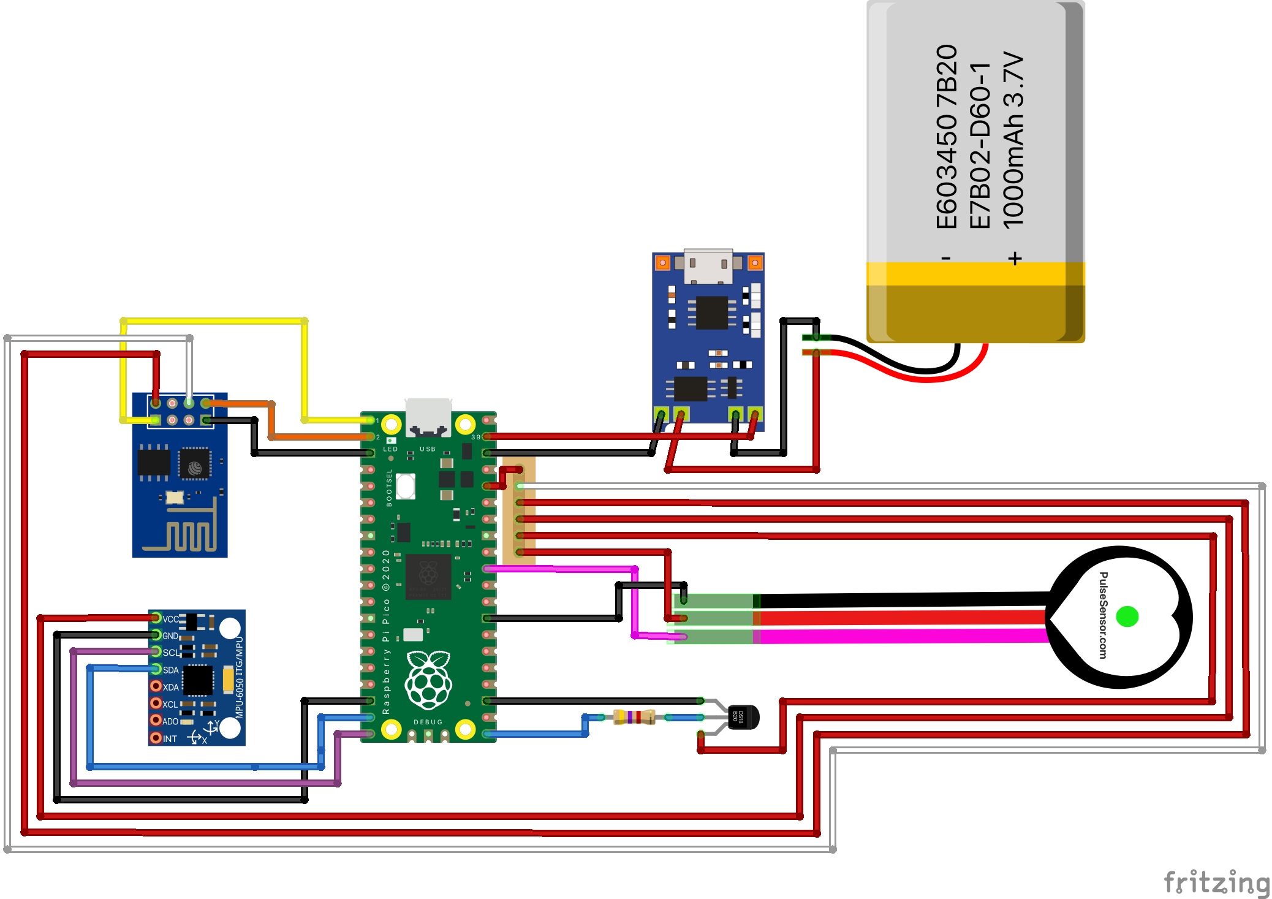
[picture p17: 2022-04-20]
Documentation/diagrama_componentes_bb.jpg

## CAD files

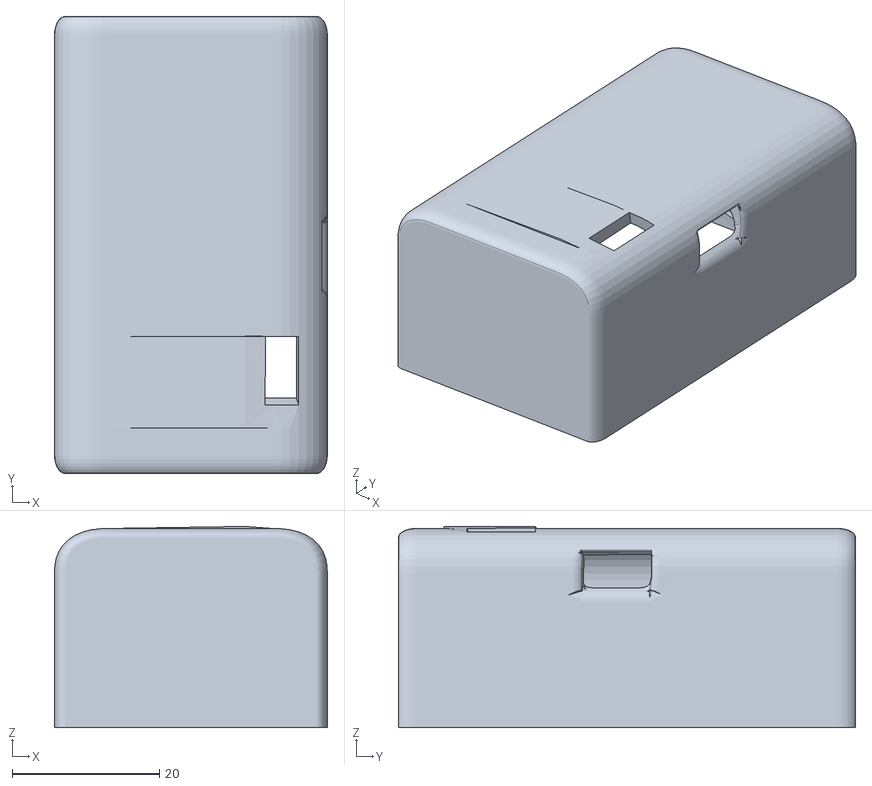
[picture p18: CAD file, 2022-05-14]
3D_Sketchs/boxV2_08.stl
37.0 x 62.0 x 27.3

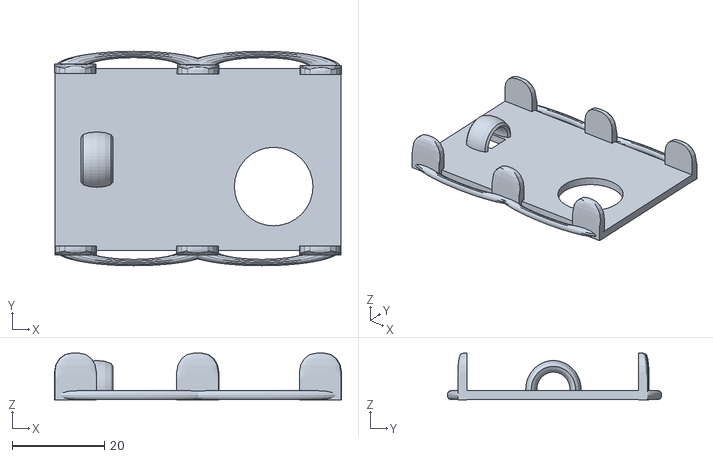
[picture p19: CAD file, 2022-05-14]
3D_Sketchs/tapaV3_01.stl
62.1 x 46.4 x 10.1

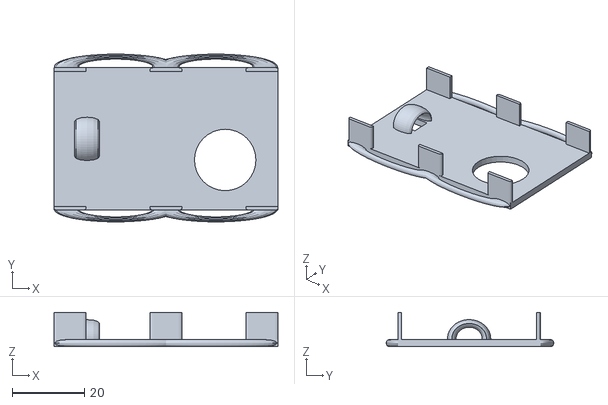
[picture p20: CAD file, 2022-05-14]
3D_Sketchs/tapaV3_1.stl
62.0 x 46.4 x 9.50

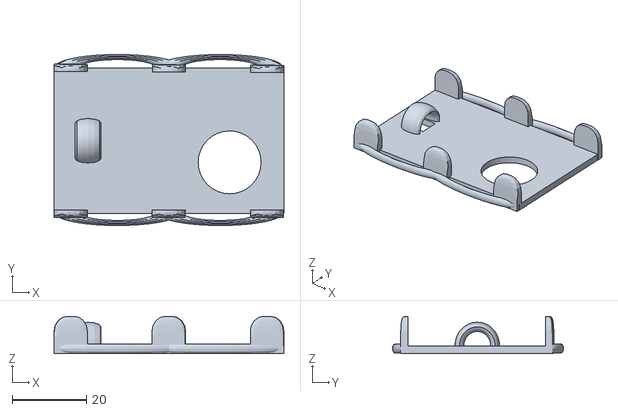
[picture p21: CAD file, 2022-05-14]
3D_Sketchs/tapaV3_02.stl
62.1 x 46.2 x 10.1

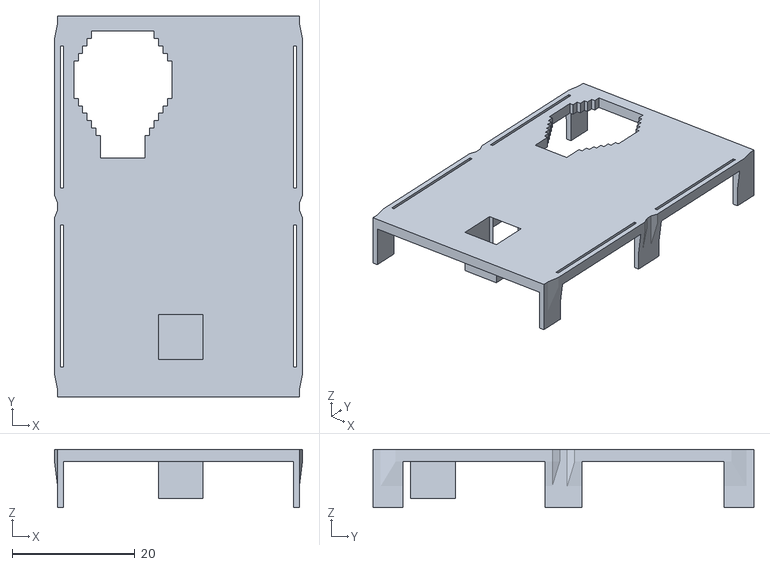
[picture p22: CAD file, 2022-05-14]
3D_Sketchs/boxV2_08_tapa.stl
40.4 x 62.0 x 9.50

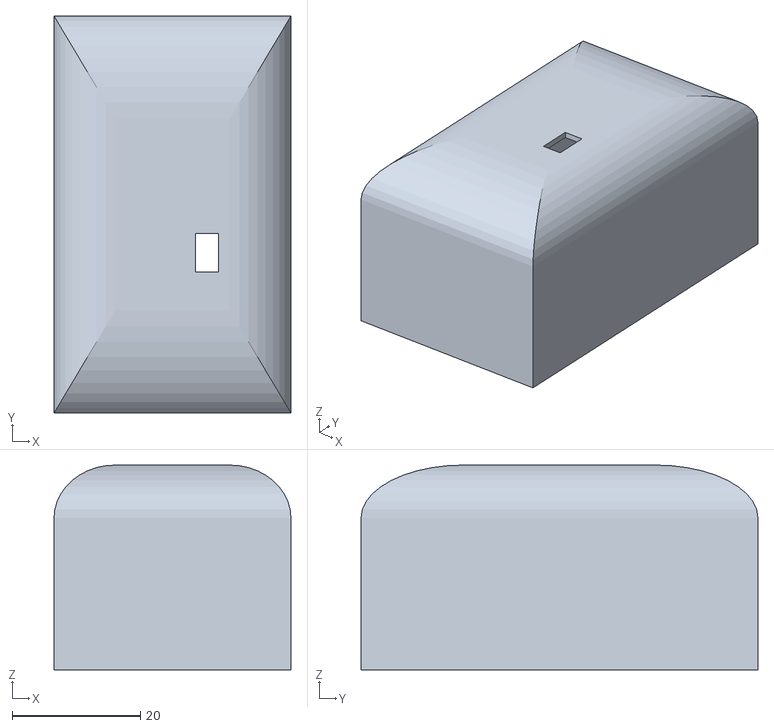
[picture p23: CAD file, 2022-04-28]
3D_Sketchs/boxV2_01_caja.stl
37.0 x 62.0 x 32.0

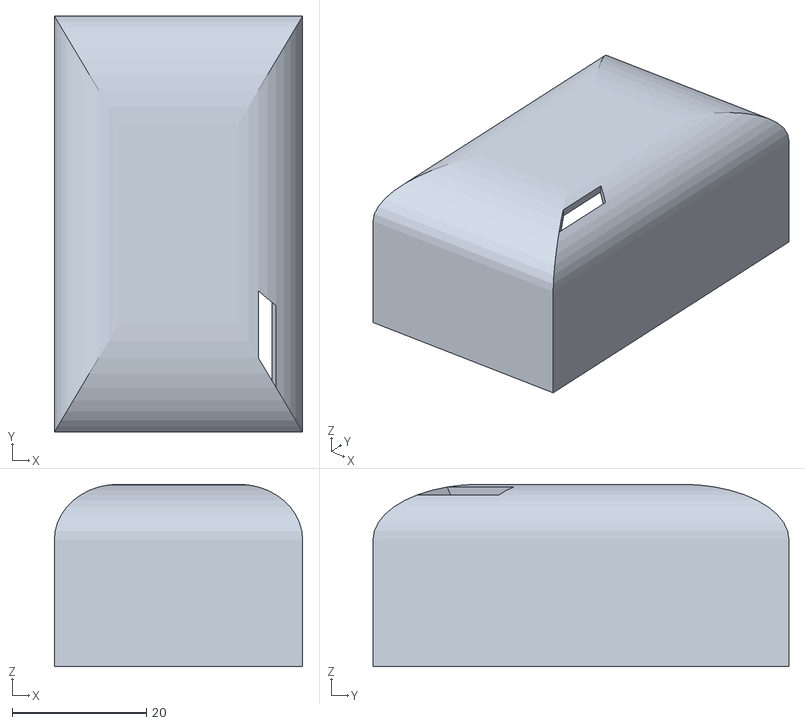
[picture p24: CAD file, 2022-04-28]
3D_Sketchs/boxV2_04_caja1.stl
37.0 x 62.0 x 27.2

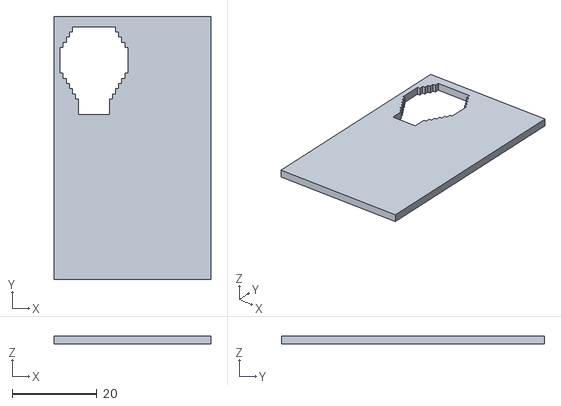
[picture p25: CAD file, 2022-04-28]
3D_Sketchs/boxV2_01_tapa.stl
37.0 x 62.0 x 2.00

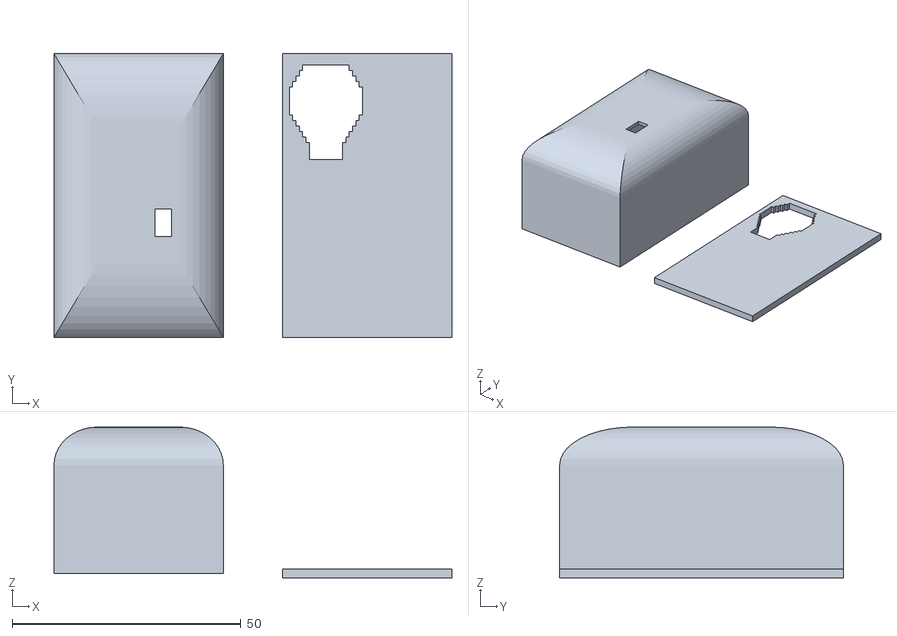
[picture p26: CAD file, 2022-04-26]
3D_Sketchs/boxV2_01.stl
87.0 x 62.0 x 33.0

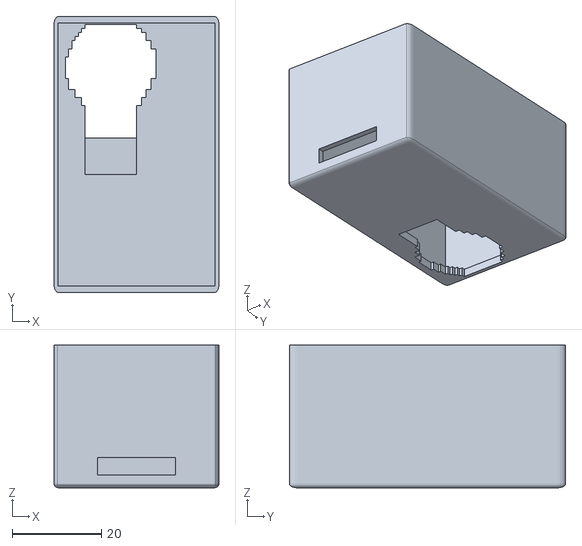
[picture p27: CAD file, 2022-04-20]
3D_Sketchs/box_04.stl
37.0 x 62.0 x 32.0

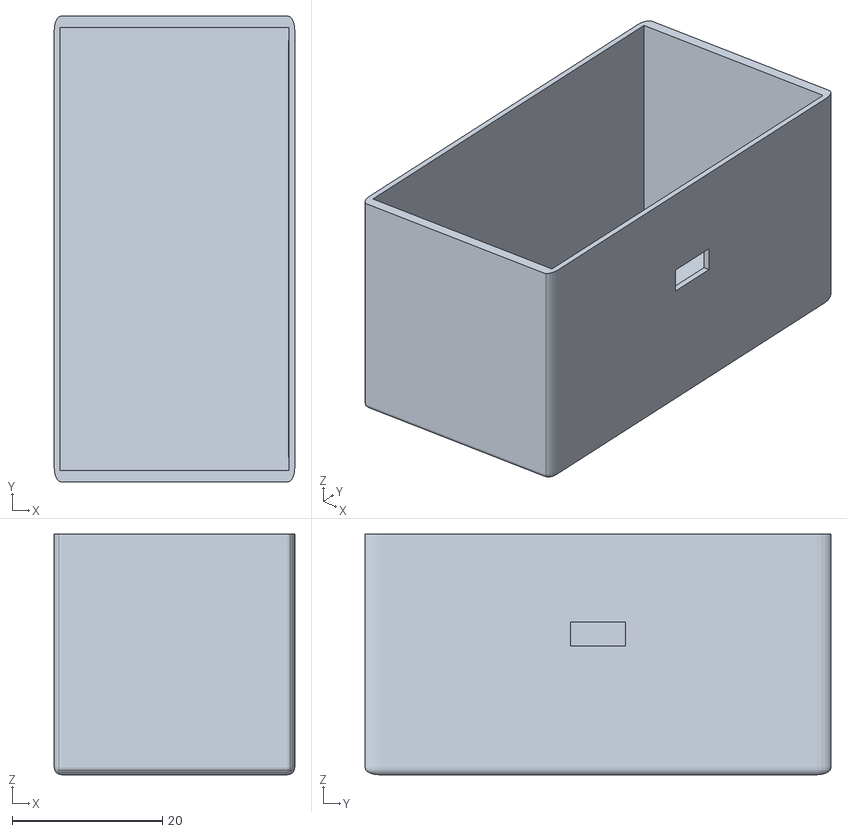
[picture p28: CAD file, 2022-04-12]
3D_Sketchs/box_02.stl
32.0 x 62.0 x 32.0

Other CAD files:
3D_Sketchs/boxV2_09.stl
3D_Sketchs/boxV2_07.stl
3D_Sketchs/boxV2_010.stl
3D_Sketchs/boxV2_06.stl
3D_Sketchs/tapaV3.stl
3D_Sketchs/boxV2_04_caja2.stl
3D_Sketchs/boxV2_02_caja.stl
3D_Sketchs/box_01.stl

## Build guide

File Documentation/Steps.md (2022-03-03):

## Pasos:

1. Planteamiento del proyecto. (si). ✅
2. Compra de los sensores y placa. (si). ✅
3. Planteamiento del pineado. (si). ✅
4. Ensamblaje en PCB de la placas placas, pico y Esp8266. Versión de trabajo. (si) ✅
5. Software y librerías de cada sensor:
    - Pulsómetro. (si) ✅
    - Temperatura. (si) ✅
    - Temperatura interna del mcu. (si) ✅
    - ~~Ecg. (si)~~
    - Acelerometro.(si) ✅
    - ~~Emg.(no)~~ 
    - ~~Oxímetro. (no)~~ 
6. Datos obtenidos de los sensores con sentido?:
    - Pulsómetro. (más o menos, hay que amplificar la señal para ciertas personas, procesado post recogida) ✅
    - Temperatura. (si) ✅
    - Temperatura interna del mcu. (si) ✅
    - ~~Ecg. (no)~~
    - Acelerometro.(si) ✅
    - ~~Emg.(no)~~ 
    - ~~Oxímetro. (no)~~ 
7. Empaquetado de datos en variable para envío al servidor.(si) ✅
8. JSON para el envio de los datos.(si) ✅
9. Software en pico para el envío de datos al servidor a través de la esp8266. (si). ✅
10. Servidor planteado. (si). ✅
11. Servidor escrito en python. (si). ✅
12. Servidor funcionanado e imprimiendo datos recibidos por pantalla. (si). ✅
13. Mejora de los tiempos de envío.(no) ✅
14. Versión tcp del conjunto.(si) ✅
15. Versión udp del conjunto.(no)❌
16. Software en el servidor representación de los datos en tiempo real.(no) ✅
17.  Ver hasta que punto llega el sampling rate.(no) ❌
18.  Planteamiento de la fuente de alimentación. Batería o Baterías. A tener en cuenta que se debe usar 5V y 3.3V.(si) ✅
19.  Opcionalmente añadir un charger module para cargar la batería.(si) ✅
20.  Después de que todo funcione correctamente planteamiento de la disposición de los sensores en el entorno, de la batería, del charger, la pico y la esp8266. Diseño definitivo.(no) ❌
21.  Ensamblaje del diseño definitivo.(no) ❌
22.  Diseño de piezas 3D para el dispositivo: 
     - Carcasa.(no) ❌
     - Pinza para pulsómetro.(si) ✅

Documentación:
1. Comparación entre arduino uno y raspberry pico. (si). ✅
2. Diagrama pin out de la raspberry pi pico para cada modulo. (si). ✅
3. Diagrama y esquemático en fritzig para la documentación. (no) ❌
4. Comparación arduinos iot y raspberry pico+Esp8266. (no) ❌
5. Comparación bitalino y mi sistema final. (no) ❌

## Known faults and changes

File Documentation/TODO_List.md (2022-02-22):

TO DO LIST:

- ~~El pin 26 es al analógico que soporta la función de ADC del código de micropython.~~

- ~~Soldar machos en la hilera que está vacía en la placa verde para hacer pruebas.~~

- ~~En la imagen de la datasheet de los pines poner cuales están ocupados y con qué~~

- ~~crear el código del acelerómetro-giroscopio.~~

- Crear Circuito de EMG (Actualización: plano buscado, componentes pedidos y esperando su llegada)

- ~~Comparación entre Arduino Nano y Raspberry Pico.~~

- ~~Soldar bien la placa ad8232~~.

- ~~Comprobar el mpu6050 en otra placa o probar otro osciloscopio en la placa, alguno falla al intentar leer el uno sobre el otro.~~ Actualización: No funciona tampoco. Pasar al siguiente paso.

- ~~Probar el mpu6050 en Arduino.~~ Actualización:Si que funciona en arduino. Conclusión: No funciona el código.

- ~~Probar otro código.~~ Actualización: Ya funciona con otro código.

- ~~Escribir el código para obtener la temperatura de la placa.~~

- Escibir código que amplifique la señal del pulsómetro.

- Comparación de pico+esp8266 con arduinos especializados en iot.

- ~~Hacer un registro de costes.~~

- Averiguar como se puede sacar el consumo de todo el conjunto para la compra de la batería.

- Hacer el diagrama de frizig, ir pensando en como encajar todo para que ocupe el menor espacio posible. 

- Ir definiendo objetivos del proyecto.

- Hacer que el tiempo de envío entre la placa y el servidor sea menor.udp?

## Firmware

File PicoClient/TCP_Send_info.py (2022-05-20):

import utime
from machine import Pin, ADC, Signal
import uos
#import utime
import rp2
from rp2 import PIO, asm_pio
#from machine import Pin
from time import sleep
import onewire
from ds18x20 import DS18X20
import binascii
import struct
import math
import utime
from machine import Pin, I2C


class MPU6050Data:

    def __init__(self):
        self.Gx=0
        self.Gy=0
        self.Gz=0
        self.Temperature=0
        self.Gyrox=0
        self.Gyroy=0
        self.Gyroz=0

class MPU6050:

    AccelerationFactor= 2.0/32768.0;   #assuming +/- 16G
    GyroFactor=500.0 / 32768.0;         #assuming 500 degree / sec

    # Temperature in degrees C = (TEMP_OUT Register Value as a signed quantity)/340 + 36.53
    TemperatureGain = 1.0 / 340.0
    TemperatureOffset = 36.53

    #converted from Jeff Rowberg code https://github.com/jrowberg/i2cdevlib/blob/master/Arduino/MPU6050/MPU6050.h


    #register definition

    MPU6050_RA_XG_OFFS_TC = 0x00 # [7] PWR_MODE, [6:1] XG_OFFS_TC, [0] OTP_BNK_VLD
    MPU6050_RA_YG_OFFS_TC = 0x01 # [7] PWR_MODE, [6:1] YG_OFFS_TC, [0] OTP_BNK_VLD
    MPU6050_RA_ZG_OFFS_TC = 0x02 # [7] PWR_MODE, [6:1] ZG_OFFS_TC, [0] OTP_BNK_VLD
    MPU6050_RA_X_FINE_GAIN = 0x03 # [7:0] X_FINE_GAIN
    MPU6050_RA_Y_FINE_GAIN = 0x04 # [7:0] Y_FINE_GAIN
    MPU6050_RA_Z_FINE_GAIN = 0x05  # [7:0] Z_FINE_GAIN
    MPU6050_RA_XA_OFFS_H = 0x06  # [15:0] XA_OFFS
    MPU6050_RA_XA_OFFS_L_TC = 0x07
    MPU6050_RA_YA_OFFS_H = 0x08  #[15:0] YA_OFFS
    MPU6050_RA_YA_OFFS_L_TC = 0x09
    MPU6050_RA_ZA_OFFS_H = 0x0A  #[15:0] ZA_OFFS
    MPU6050_RA_ZA_OFFS_L_TC = 0x0B
    MPU6050_RA_XG_OFFS_USRH = 0x13  #[15:0] XG_OFFS_USR
    MPU6050_RA_XG_OFFS_USRL = 0x14
    MPU6050_RA_YG_OFFS_USRH = 0x15  #[15:0] YG_OFFS_USR
    MPU6050_RA_YG_OFFS_USRL = 0x16
    MPU6050_RA_ZG_OFFS_USRH = 0x17  #[15:0] ZG_OFFS_USR
    MPU6050_RA_ZG_OFFS_USRL = 0x18
    MPU6050_RA_SMPLRT_DIV = 0x19
    MPU6050_RA_CONFIG = 0x1A
    MPU6050_RA_GYRO_CONFIG = 0x1B
    MPU6050_RA_ACCEL_CONFIG = 0x1C
    MPU6050_RA_FF_THR = 0x1D
    MPU6050_RA_FF_DUR = 0x1E
    MPU6050_RA_MOT_THR = 0x1F
    MPU6050_RA_MOT_DUR = 0x20
    MPU6050_RA_ZRMOT_THR = 0x21
    MPU6050_RA_ZRMOT_DUR = 0x22
    MPU6050_RA_FIFO_EN = 0x23
    MPU6050_RA_I2C_MST_CTRL = 0x24
    MPU6050_RA_I2C_SLV0_ADDR = 0x25
    MPU6050_RA_I2C_SLV0_REG = 0x26
    MPU6050_RA_I2C_SLV0_CTRL = 0x27
    MPU6050_RA_I2C_SLV1_ADDR = 0x28
    MPU6050_RA_I2C_SLV1_REG = 0x29
    MPU6050_RA_I2C_SLV1_CTRL = 0x2A
    MPU6050_RA_I2C_SLV2_ADDR = 0x2B
    MPU6050_RA_I2C_SLV2_REG = 0x2C
    MPU6050_RA_I2C_SLV2_CTRL = 0x2D
    MPU6050_RA_I2C_SLV3_ADDR = 0x2E
    MPU6050_RA_I2C_SLV3_REG = 0x2F
    MPU6050_RA_I2C_SLV3_CTRL = 0x30
    MPU6050_RA_I2C_SLV4_ADDR = 0x31
    MPU6050_RA_I2C_SLV4_REG = 0x32
    MPU6050_RA_I2C_SLV4_DO = 0x33
    MPU6050_RA_I2C_SLV4_CTRL = 0x34
    MPU6050_RA_I2C_SLV4_DI = 0x35
    MPU6050_RA_I2C_MST_STATUS = 0x36
    MPU6050_RA_INT_PIN_CFG = 0x37
    MPU6050_RA_INT_ENABLE = 0x38
    MPU6050_RA_DMP_INT_STATUS = 0x39
    MPU6050_RA_INT_STATUS = 0x3A
    MPU6050_RA_ACCEL_XOUT_H = 0x3B
    MPU6050_RA_ACCEL_XOUT_L = 0x3C
    MPU6050_RA_ACCEL_YOUT_H = 0x3D
    MPU6050_RA_ACCEL_YOUT_L = 0x3E
    MPU6050_RA_ACCEL_ZOUT_H = 0x3F
    MPU6050_RA_ACCEL_ZOUT_L = 0x40
    MPU6050_RA_TEMP_OUT_H = 0x41
    MPU6050_RA_TEMP_OUT_L = 0x42
    MPU6050_RA_GYRO_XOUT_H = 0x43
    MPU6050_RA_GYRO_XOUT_L = 0x44
    MPU6050_RA_GYRO_YOUT_H = 0x45
    MPU6050_RA_GYRO_YOUT_L = 0x46
    MPU6050_RA_GYRO_ZOUT_H = 0x47
    MPU6050_RA_GYRO_ZOUT_L = 0x48
    MPU6050_RA_EXT_SENS_DATA_00 = 0x49
    MPU6050_RA_EXT_SENS_DATA_01 = 0x4A
    MPU6050_RA_EXT_SENS_DATA_02 = 0x4B
    MPU6050_RA_EXT_SENS_DATA_03 = 0x4C
    MPU6050_RA_EXT_SENS_DATA_04 = 0x4D
    MPU6050_RA_EXT_SENS_DATA_05 = 0x4E
    MPU6050_RA_EXT_SENS_DATA_06 = 0x4F
    MPU6050_RA_EXT_SENS_DATA_07 = 0x50
    MPU6050_RA_EXT_SENS_DATA_08 = 0x51
    MPU6050_RA_EXT_SENS_DATA_09 = 0x52
    MPU6050_RA_EXT_SENS_DATA_10 = 0x53
    MPU6050_RA_EXT_SENS_DATA_11 = 0x54
    MPU6050_RA_EXT_SENS_DATA_12 = 0x55
    MPU6050_RA_EXT_SENS_DATA_13 = 0x56
    MPU6050_RA_EXT_SENS_DATA_14 = 0x57
    MPU6050_RA_EXT_SENS_DATA_15 = 0x58
    MPU6050_RA_EXT_SENS_DATA_16 = 0x59
    MPU6050_RA_EXT_SENS_DATA_17 = 0x5A
    MPU6050_RA_EXT_SENS_DATA_18 = 0x5B
    MPU6050_RA_EXT_SENS_DATA_19 = 0x5C
    MPU6050_RA_EXT_SENS_DATA_20 = 0x5D
    MPU6050_RA_EXT_SENS_DATA_21 = 0x5E
    MPU6050_RA_EXT_SENS_DATA_22 = 0x5F
    MPU6050_RA_EXT_SENS_DATA_23 = 0x60
    MPU6050_RA_MOT_DETECT_STATUS = 0x61
    MPU6050_RA_I2C_SLV0_DO = 0x63
    MPU6050_RA_I2C_SLV1_DO = 0x64
    MPU6050_RA_I2C_SLV2_DO = 0x65
    MPU6050_RA_I2C_SLV3_DO = 0x66
    MPU6050_RA_I2C_MST_DELAY_CTRL = 0x67
    MPU6050_RA_SIGNAL_PATH_RESET = 0x68
    MPU6050_RA_MOT_DETECT_CTRL = 0x69
    MPU6050_RA_USER_CTRL = 0x6A
    MPU6050_RA_PWR_MGMT_1 = 0x6B
    MPU6050_RA_PWR_MGMT_2 = 0x6C
    MPU6050_RA_BANK_SEL = 0x6D
    MPU6050_RA_MEM_START_ADDR = 0x6E
    MPU6050_RA_MEM_R_W = 0x6F
    MPU6050_RA_DMP_CFG_1 = 0x70
    MPU6050_RA_DMP_CFG_2 = 0x71
    MPU6050_RA_FIFO_COUNTH = 0x72
    MPU6050_RA_FIFO_COUNTL = 0x73
    MPU6050_RA_FIFO_R_W = 0x74
    MPU6050_RA_WHO_AM_I = 0x75     

    ZeroRegister = [
        MPU6050_RA_FF_THR, #Freefall threshold of |0mg|  LDByteWriteI2C(MPU6050_ADDRESS, MPU6050_RA_FF_THR, 0x00);
        MPU6050_RA_FF_DUR, #Freefall duration limit of 0   LDByteWriteI2C(MPU6050_ADDRESS, MPU6050_RA_FF_DUR, 0x00);
        MPU6050_RA_MOT_THR, #Motion threshold of 0mg     LDByteWriteI2C(MPU6050_ADDRESS, MPU6050_RA_MOT_THR, 0x00);
        MPU6050_RA_MOT_DUR, #Motion duration of 0s    LDByteWriteI2C(MPU6050_ADDRESS, MPU6050_RA_MOT_DUR, 0x00);
        MPU6050_RA_ZRMOT_THR, #Zero motion threshold    LDByteWriteI2C(MPU6050_ADDRESS, MPU6050_RA_ZRMOT_THR, 0x00);
        MPU6050_RA_ZRMOT_DUR, #Zero motion duration threshold    LDByteWriteI2C(MPU6050_ADDRESS, MPU6050_RA_ZRMOT_DUR, 0x00);
        MPU6050_RA_FIFO_EN, #Disable sensor output to FIFO buffer    LDByteWriteI2C(MPU6050_ADDRESS, MPU6050_RA_FIFO_EN, 0x00);
        MPU6050_RA_I2C_MST_CTRL, #AUX I2C setup    //Sets AUX I2C to single master control, plus other config    LDByteWriteI2C(MPU6050_ADDRESS, MPU6050_RA_I2C_MST_CTRL, 0x00);
        MPU6050_RA_I2C_SLV0_ADDR, #Setup AUX I2C slaves    LDByteWriteI2C(MPU6050_ADDRESS, MPU6050_RA_I2C_SLV0_ADDR, 0x00);
        MPU6050_RA_I2C_SLV0_REG, #LDByteWriteI2C(MPU6050_ADDRESS, MPU6050_RA_I2C_SLV0_REG, 0x00);
        MPU6050_RA_I2C_SLV0_CTRL, #LDByteWriteI2C(MPU6050_ADDRESS, MPU6050_RA_I2C_SLV0_CTRL, 0x00);
        MPU6050_RA_I2C_SLV1_ADDR, #LDByteWriteI2C(MPU6050_ADDRESS, MPU6050_RA_I2C_SLV1_ADDR, 0x00);
        MPU6050_RA_I2C_SLV1_REG, #LDByteWriteI2C(MPU6050_ADDRESS, MPU6050_RA_I2C_SLV1_REG, 0x00);
        MPU6050_RA_I2C_SLV1_CTRL, #LDByteWriteI2C(MPU6050_ADDRESS, MPU6050_RA_I2C_SLV1_CTRL, 0x00);
        MPU6050_RA_I2C_SLV2_ADDR, #LDByteWriteI2C(MPU6050_ADDRESS, MPU6050_RA_I2C_SLV2_ADDR, 0x00);
        MPU6050_RA_I2C_SLV2_REG, #LDByteWriteI2C(MPU6050_ADDRESS, MPU6050_RA_I2C_SLV2_REG, 0x00);
        MPU6050_RA_I2C_SLV2_CTRL, #LDByteWriteI2C(MPU6050_ADDRESS, MPU6050_RA_I2C_SLV2_CTRL, 0x00);
        MPU6050_RA_I2C_SLV3_ADDR, #LDByteWriteI2C(MPU6050_ADDRESS, MPU6050_RA_I2C_SLV3_ADDR, 0x00);
        MPU6050_RA_I2C_SLV3_REG, #LDByteWriteI2C(MPU6050_ADDRESS, MPU6050_RA_I2C_SLV3_REG, 0x00);
        MPU6050_RA_I2C_SLV3_CTRL, #LDByteWriteI2C(MPU6050_ADDRESS, MPU6050_RA_I2C_SLV3_CTRL, 0x00);
        MPU6050_RA_I2C_SLV4_ADDR, #LDByteWriteI2C(MPU6050_ADDRESS, MPU6050_RA_I2C_SLV4_ADDR, 0x00);
        MPU6050_RA_I2C_SLV4_REG, #LDByteWriteI2C(MPU6050_ADDRESS, MPU6050_RA_I2C_SLV4_REG, 0x00);
        MPU6050_RA_I2C_SLV4_DO, #LDByteWriteI2C(MPU6050_ADDRESS, MPU6050_RA_I2C_SLV4_DO, 0x00);
        MPU6050_RA_I2C_SLV4_CTRL, #LDByteWriteI2C(MPU6050_ADDRESS, MPU6050_RA_I2C_SLV4_CTRL, 0x00);
        MPU6050_RA_I2C_SLV4_DI, #LDByteWriteI2C(MPU6050_ADDRESS, MPU6050_RA_I2C_SLV4_DI, 0x00);
        MPU6050_RA_INT_PIN_CFG, #MPU6050_RA_I2C_MST_STATUS //Read-only    //Setup INT pin and AUX I2C pass through    LDByteWriteI2C(MPU6050_ADDRESS, MPU6050_RA_INT_PIN_CFG, 0x00);
        MPU6050_RA_INT_ENABLE, #Enable data ready interrupt      LDByteWriteI2C(MPU6050_ADDRESS, MPU6050_RA_INT_ENABLE, 0x00);
        MPU6050_RA_I2C_SLV0_DO, #Slave out, dont care    LDByteWriteI2C(MPU6050_ADDRESS, MPU6050_RA_I2C_SLV0_DO, 0x00);
        MPU6050_RA_I2C_SLV1_DO, #LDByteWriteI2C(MPU6050_ADDRESS, MPU6050_RA_I2C_SLV1_DO, 0x00);
        MPU6050_RA_I2C_SLV2_DO, #LDByteWriteI2C(MPU6050_ADDRESS, MPU6050_RA_I2C_SLV2_DO, 0x00);
        MPU6050_RA_I2C_SLV3_DO, #LDByteWriteI2C(MPU6050_ADDRESS, MPU6050_RA_I2C_SLV3_DO, 0x00);
        MPU6050_RA_I2C_MST_DELAY_CTRL, #More slave config      LDByteWriteI2C(MPU6050_ADDRESS, MPU6050_RA_I2C_MST_DELAY_CTRL, 0x00);
        MPU6050_RA_SIGNAL_PATH_RESET, #Reset sensor signal paths    LDByteWriteI2C(MPU6050_ADDRESS, MPU6050_RA_SIGNAL_PATH_RESET, 0x00);
        MPU6050_RA_MOT_DETECT_CTRL, #Motion detection control    LDByteWriteI2C(MPU6050_ADDRESS, MPU6050_RA_MOT_DETECT_CTRL, 0x00);
        MPU6050_RA_USER_CTRL, #Disables FIFO, AUX I2C, FIFO and I2C reset bits to 0    LDByteWriteI2C(MPU6050_ADDRESS, MPU6050_RA_USER_CTRL, 0x00);
        MPU6050_RA_CONFIG, #Disable FSync, 256Hz DLPF    LDByteWriteI2C(MPU6050_ADDRESS, MPU6050_RA_CONFIG, 0x00);
        MPU6050_RA_FF_THR, #Freefall threshold of |0mg|    LDByteWriteI2C(MPU6050_ADDRESS, MPU6050_RA_FF_THR, 0x00);
        MPU6050_RA_FF_DUR, #Freefall duration limit of 0    LDByteWriteI2C(MPU6050_ADDRESS, MPU6050_RA_FF_DUR, 0x00);
        MPU6050_RA_MOT_THR, #Motion threshold of 0mg    LDByteWriteI2C(MPU6050_ADDRESS, MPU6050_RA_MOT_THR, 0x00);
        MPU6050_RA_MOT_DUR, #Motion duration of 0s    LDByteWriteI2C(MPU6050_ADDRESS, MPU6050_RA_MOT_DUR, 0x00);
        MPU6050_RA_ZRMOT_THR, #Zero motion threshold    LDByteWriteI2C(MPU6050_ADDRESS, MPU6050_RA_ZRMOT_THR, 0x00);
        MPU6050_RA_ZRMOT_DUR, #Zero motion duration threshold    LDByteWriteI2C(MPU6050_ADDRESS, MPU6050_RA_ZRMOT_DUR, 0x00);
        MPU6050_RA_FIFO_EN, #Disable sensor output to FIFO buffer    LDByteWriteI2C(MPU6050_ADDRESS, MPU6050_RA_FIFO_EN, 0x00);
        MPU6050_RA_I2C_MST_CTRL, #AUX I2C setup    //Sets AUX I2C to single master control, plus other config    LDByteWriteI2C(MPU6050_ADDRESS, MPU6050_RA_I2C_MST_CTRL, 0x00);
        MPU6050_RA_I2C_SLV0_ADDR, #Setup AUX I2C slaves    LDByteWriteI2C(MPU6050_ADDRESS, MPU6050_RA_I2C_SLV0_ADDR, 0x00);
        MPU6050_RA_I2C_SLV0_REG, #LDByteWriteI2C(MPU6050_ADDRESS, MPU6050_RA_I2C_SLV0_REG, 0x00);
        MPU6050_RA_I2C_SLV0_CTRL, #LDByteWriteI2C(MPU6050_ADDRESS, MPU6050_RA_I2C_SLV0_CTRL, 0x00);
        MPU6050_RA_I2C_SLV1_ADDR, #LDByteWriteI2C(MPU6050_ADDRESS, MPU6050_RA_I2C_SLV1_ADDR, 0x00);
        MPU6050_RA_I2C_SLV1_REG, #LDByteWriteI2C(MPU6050_ADDRESS, MPU6050_RA_I2C_SLV1_REG, 0x00);
        MPU6050_RA_I2C_SLV1_CTRL, #LDByteWriteI2C(MPU6050_ADDRESS, MPU6050_RA_I2C_SLV1_CTRL, 0x00);
        MPU6050_RA_I2C_SLV2_ADDR, #LDByteWriteI2C(MPU6050_ADDRESS, MPU6050_RA_I2C_SLV2_ADDR, 0x00);
        MPU6050_RA_I2C_SLV2_REG, #LDByteWriteI2C(MPU6050_ADDRESS, MPU6050_RA_I2C_SLV2_REG, 0x00);
        MPU6050_RA_I2C_SLV2_CTRL, #LDByteWriteI2C(MPU6050_ADDRESS, MPU6050_RA_I2C_SLV2_CTRL, 0x00);
        MPU6050_RA_I2C_SLV3_ADDR, #LDByteWriteI2C(MPU6050_ADDRESS, MPU6050_RA_I2C_SLV3_ADDR, 0x00);
        MPU6050_RA_I2C_SLV3_REG, #LDByteWriteI2C(MPU6050_ADDRESS, MPU6050_RA_I2C_SLV3_REG, 0x00);
        MPU6050_RA_I2C_SLV3_CTRL, #LDByteWriteI2C(MPU6050_ADDRESS, MPU6050_RA_I2C_SLV3_CTRL, 0x00);
        MPU6050_RA_I2C_SLV4_ADDR, #LDByteWriteI2C(MPU6050_ADDRESS, MPU6050_RA_I2C_SLV4_ADDR, 0x00);
        MPU6050_RA_I2C_SLV4_REG, #LDByteWriteI2C(MPU6050_ADDRESS, MPU6050_RA_I2C_SLV4_REG, 0x00);
        MPU6050_RA_I2C_SLV4_DO, #LDByteWriteI2C(MPU6050_ADDRESS, MPU6050_RA_I2C_SLV4_DO, 0x00);
        MPU6050_RA_I2C_SLV4_CTRL, #LDByteWriteI2C(MPU6050_ADDRESS, MPU6050_RA_I2C_SLV4_CTRL, 0x00);
        MPU6050_RA_I2C_SLV4_DI, #LDByteWriteI2C(MPU6050_ADDRESS, MPU6050_RA_I2C_SLV4_DI, 0x00);
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

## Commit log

2022-02-16 subida de todo
2022-02-21 socket in pico
2022-04-28 new sketchs
    [boxV2_01.blend, boxV2_01_caja.stl, boxV2_01_tapa.stl, boxV2_02.blend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]
